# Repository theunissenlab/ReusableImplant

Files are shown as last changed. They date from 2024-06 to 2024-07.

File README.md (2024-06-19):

# Chronic Reusable Implant Parts List and Instructions

Both .stl and .sldprt files have been included for your convinence. All SLDPRT files were made on SOLIDWORKS 2022.

## Implant Parts List

In this repository are all the parts required to build the chronic implant. It is made for use with the Cambridge Neurotech Mini-Amp and silicon probes. All parts were printed on FormLabs Form 3+. Specific printing instructions including resin type, density, and touchpoint size are detailed depending on the part.

- [Payload](https://github.com/AnnLiBenn/ReusableImplant/blob/main/README.md#payload)
- [Docking](https://github.com/AnnLiBenn/ReusableImplant/blob/main/README.md#Docking)
- [Amplifier Holder](https://github.com/AnnLiBenn/ReusableImplant/blob/main/README.md#amplifier-holder)
- [Headstage Cover](https://github.com/AnnLiBenn/ReusableImplant/blob/main/README.md#headstage-cover)
- [Payload Holder](https://github.com/AnnLiBenn/ReusableImplant/blob/main/README.md#payload-holder)
- [Docking Holder](https://github.com/AnnLiBenn/ReusableImplant/blob/main/README.md#docking-holder)
- [Support Base](https://github.com/AnnLiBenn/ReusableImplant/blob/main/README.md#support-base)

### Payload

This is the module that holds the probe. It is re-used across implantations. Print in Rigid resin with density at 80 and touchpoint size at 0.4mm.

<p align="center">
Screenshot 2024-06-19 at 3 01 42 PM

</p>

### Docking

This is the module that is cemented to the skull after being screwed to the payload module. A new docking module is required for each implantation. Print in Rigid resin with density at 80 and touchpoint size at 0.4mm.

<p align="center">
Screenshot 2024-06-19 at 3 02 54 PM

</p>

### Amplifier Holder

This is the module that inserts into the payload in order to hold and stablilize the amplifier. It is re-used across implantations. Print in Rigid resin with density at 80 and touchpoint size at 0.4mm.

<p align="center">
Screenshot 2024-06-19 at 3 03 33 PM

</p>

### Headstage Cover

This is the cover for the implant. It protects the flex cable between the probe and amplifier. It is re-used across implantations. Print in Black resin with density 90 and touchpoint size at 0.4mm.

<p align="center">
Screenshot 2024-06-19 at 3 04 15 PM

</p>

### Assembly Jig Parts List

In this section are all the parts needed to create the jig for assembly.

## Payload Holder

This is a holder that can is inserted into the payload module during assembly so that the payload module is centered. Print in Black resin with density 80 and touchpoint size at 0.45mm.

<p align="center">
Screenshot 2024-06-19 at 3 06 48 PM

</p>

### Docking Holder

This is a holder that holds the docking module in place when using the jig to combine the two modules. Print in Black resin with density 80 and touchpoint size at 0.45mm.

<p align="center">
Screenshot 2024-06-19 at 3 07 34 PM

</p>

### Support Base

This is the base of the assembly jig. It is used to secure the rods. Print in Black resin with density 80 and touchpoint size at 0.45mm.

<p align="center">
Screenshot 2024-06-19 at 3 07 56 PM
</p>

### Rod Attachment

This is an attachment for a rod to hold the payload module. Print in Black resin density 80 and touchpoint size 0.40mm.

<p align="center">
Screenshot 2024-06-19 at 3 11 28 PM
</p>

### Assembly Diagrams

This is the complete implant assembly.

<p align="center">
Screenshot 2024-06-19 at 3 09 19 PM
Screenshot 2024-06-19 at 3 10 05 PM

</p>

## Additional Parts:

Note: Links are for reference, but could be sourced elsewhere. The brass inserts are heat inserted using a soldering iron and mild pressure.

- [M1 Brass knurled inserts](https://www.ebay.co.uk/itm/124738465135) (5x): To be heat-inserted into the Payload.

- [M3 Brass knurled inserts](https://www.mcmaster.com/94459A140/) (6x): To be heat-inserted into the Docking Holder and support base.
  
- [M1 Screws](https://www.mcmaster.com/91800A050/) (5x): To lock modules together.

- [M3 10mm screws](https://www.mcmaster.com/91290A295/) (6x): For securing the Docking Module in its holder, and the rods in the support base

- 6.4mm diameter rods: For creating the assembly jig

## Cleaning Instructions

This is a cleaning cap for the cleaning of the probes after use. It is designed to screw on to 20mL vial.

<p align="center">
Screenshot 2024-06-19 at 3 10 26 PM

</p>

## Note
All .sldprt files were created using SOLIDWORKS 2022. This design is inspired by the [Coen-Lab Apollo Implant](https://github.com/Coen-Lab/chronic-neuropixels/tree/main#np1_payload-or-np2-alpha_payload).

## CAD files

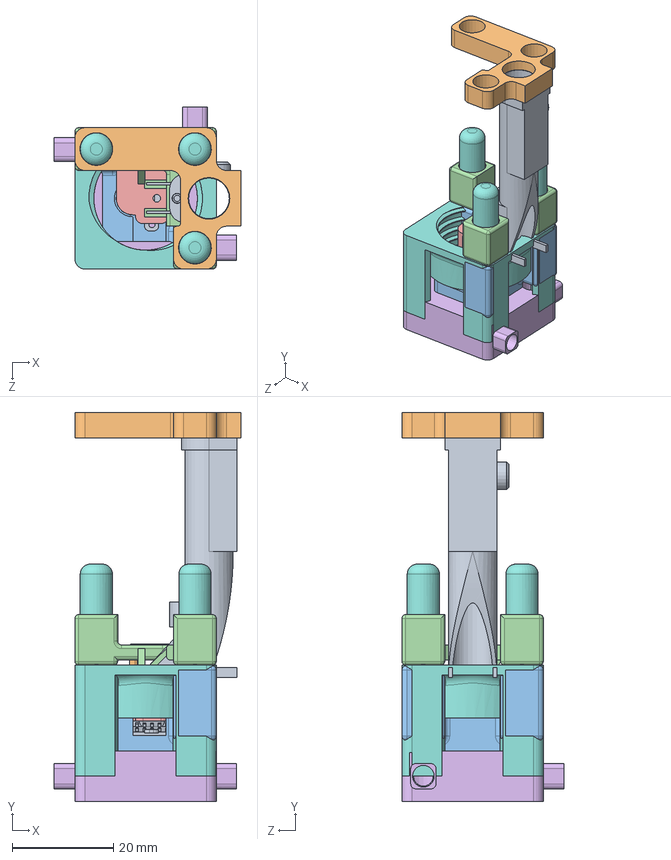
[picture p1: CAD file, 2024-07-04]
ImplantSLDPRT/HeadstageAssembly.SLDASM
36.9 x 77.0 x 32.1 mm
SupportBase
Payload
RodAttachmentRigid
RodGuide

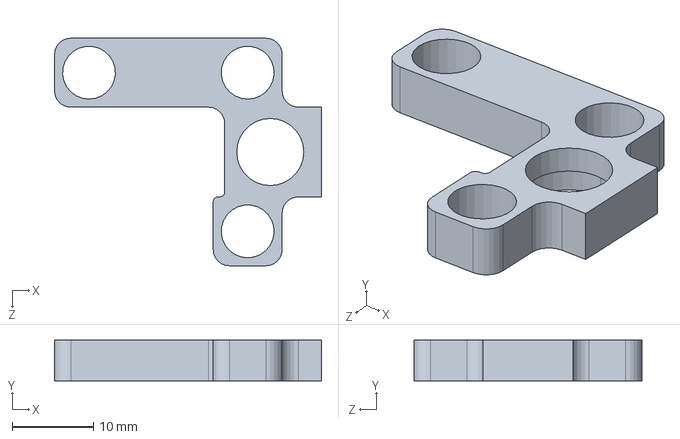
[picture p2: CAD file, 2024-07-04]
ImplantSLDPRT/RodGuide.SLDPRT
32.8 x 5.00 x 28.0 mm

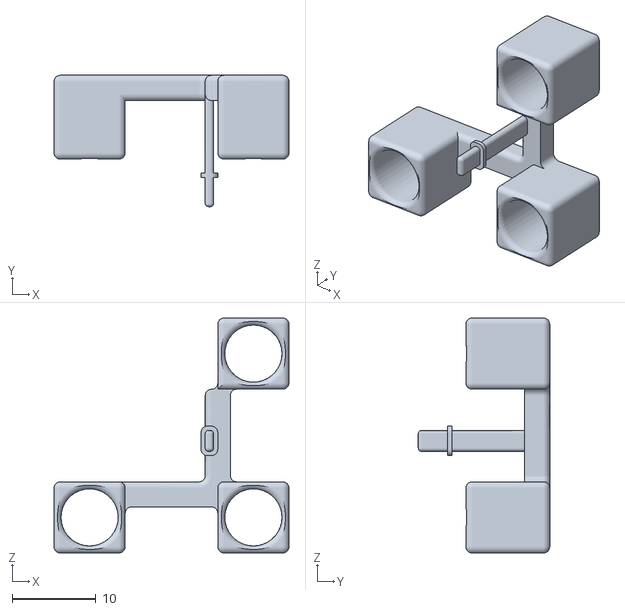
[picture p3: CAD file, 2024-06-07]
ImplantSTL/Payload Holder v3.STL
28.0 x 15.7 x 28.0

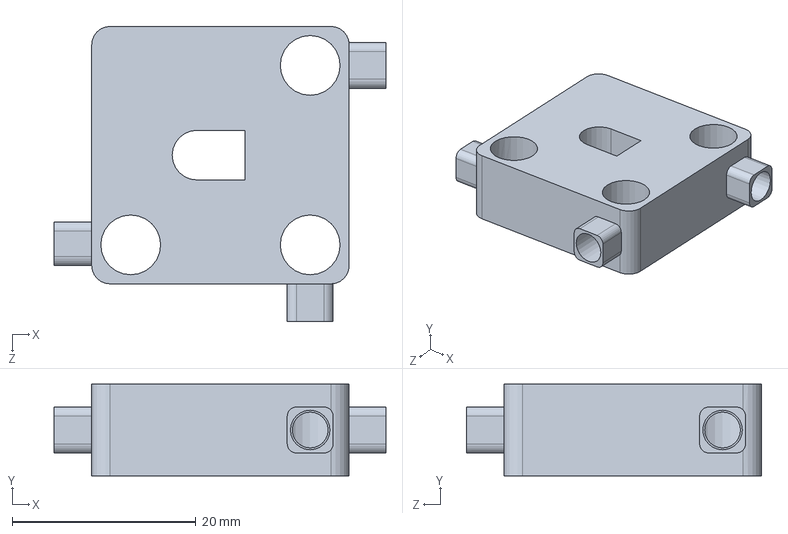
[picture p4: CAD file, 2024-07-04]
ImplantSLDPRT/SupportBase.SLDPRT
36.1 x 10.0 x 32.1 mm

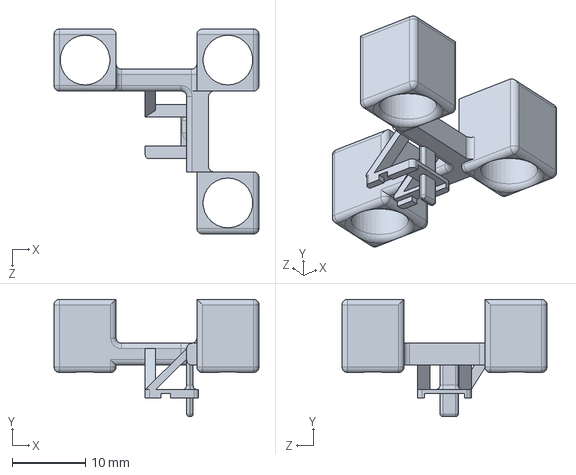
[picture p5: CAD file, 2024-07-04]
ImplantSLDPRT/PayloadHolder.SLDPRT
28.0 x 16.0 x 28.0 mm

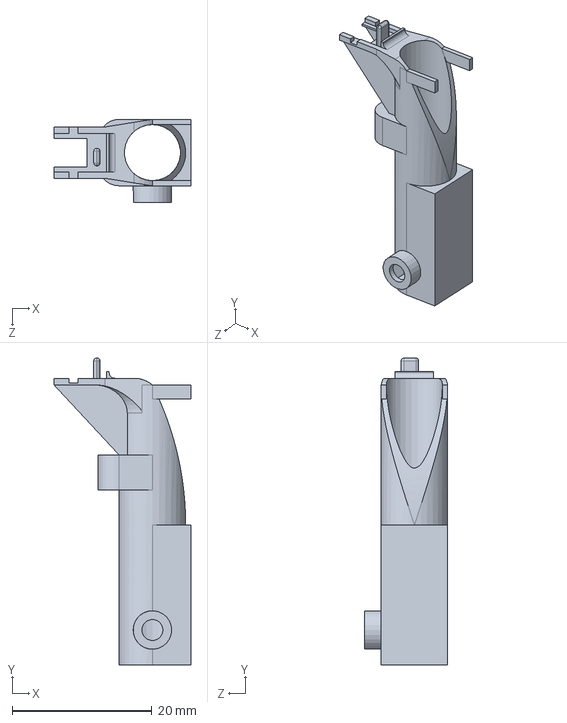
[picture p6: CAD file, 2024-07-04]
ImplantSLDPRT/RodAttachment.SLDPRT
19.6 x 43.9 x 11.9 mm

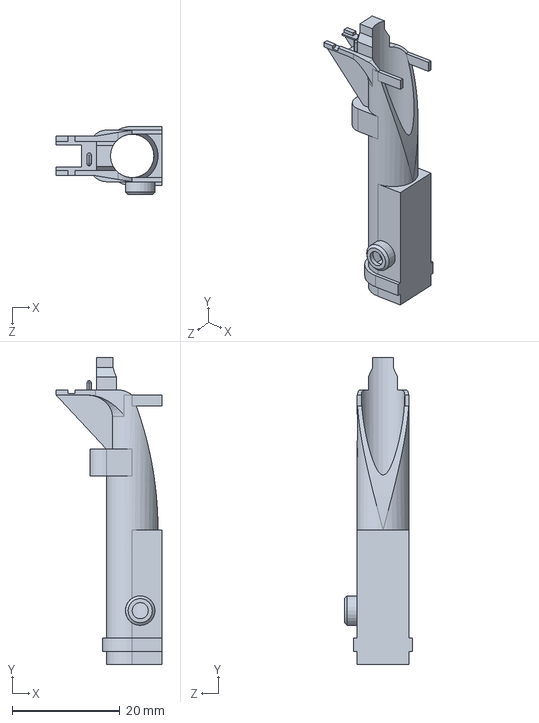
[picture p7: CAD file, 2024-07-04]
ImplantSLDPRT/RodAttachmentRigid.SLDPRT
19.6 x 57.0 x 12.7 mm

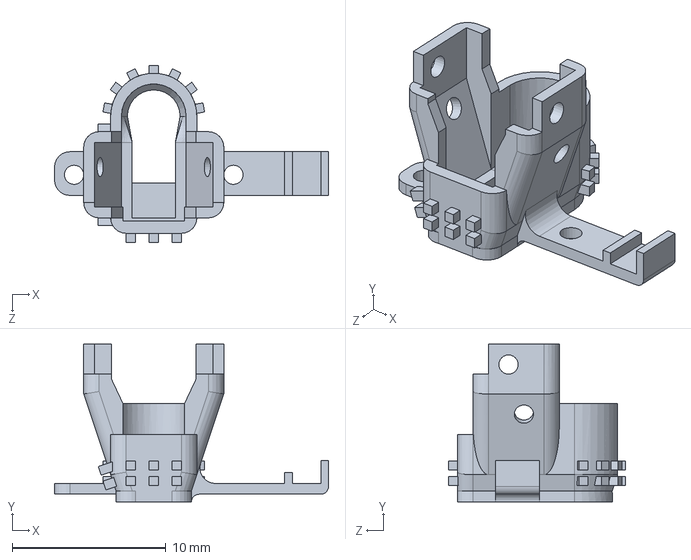
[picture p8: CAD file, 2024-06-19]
ImplantSLDPRT/Docking.SLDPRT
17.8 x 10.2 x 11.5 mm

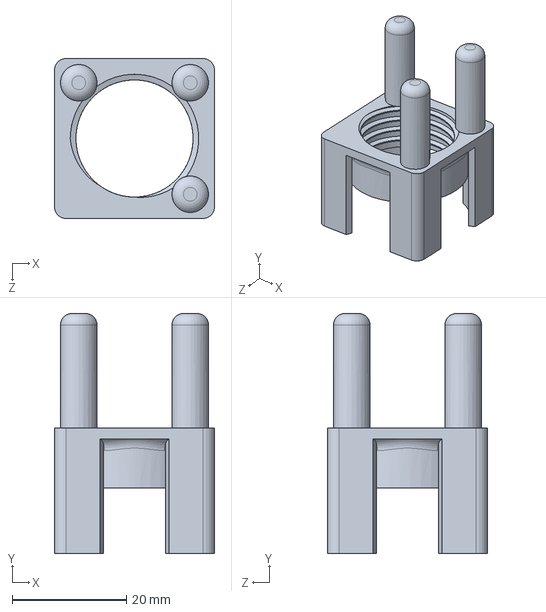
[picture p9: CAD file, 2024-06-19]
ImplantSLDPRT/CleaningCap.SLDPRT
28.0 x 42.0 x 28.0 mm

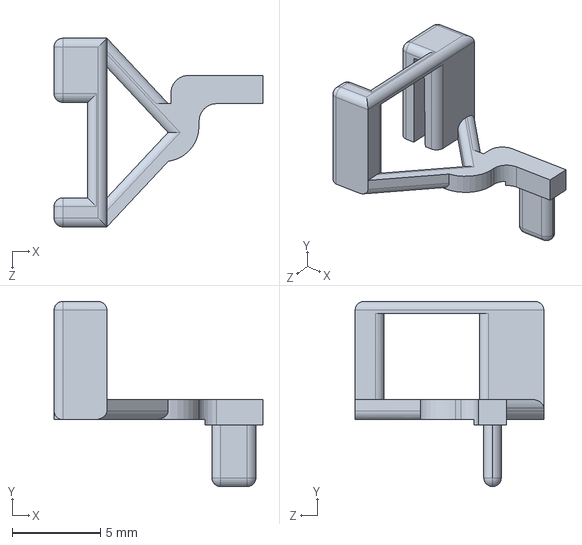
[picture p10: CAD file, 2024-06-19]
ImplantSLDPRT/AmplifierHolder.SLDPRT
11.8 x 10.5 x 10.7 mm

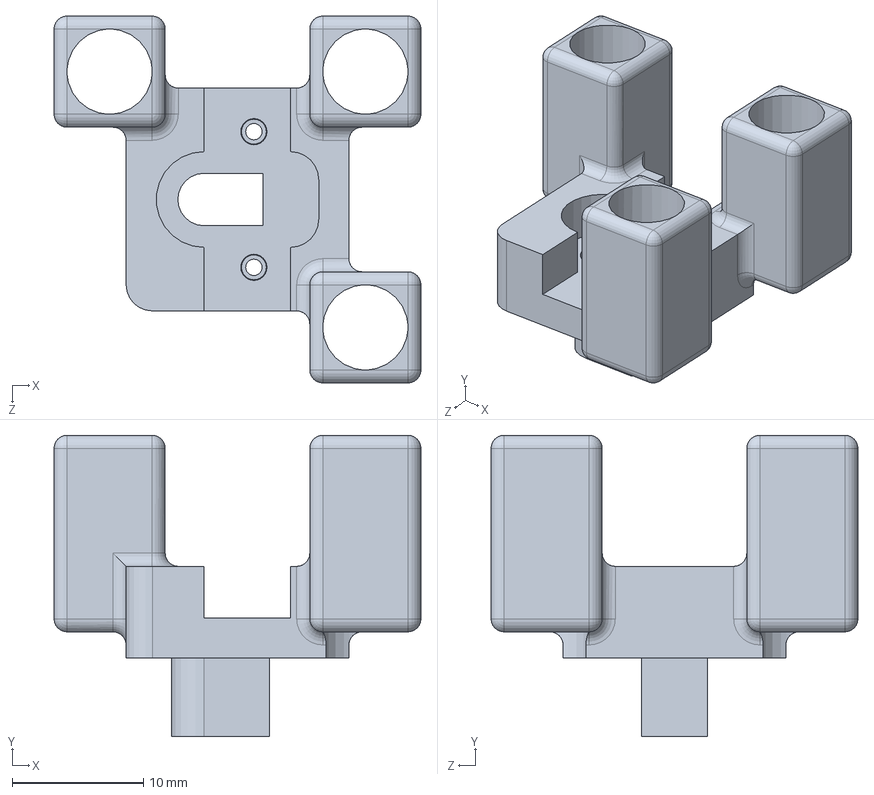
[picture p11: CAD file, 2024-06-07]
ImplantSLDPRT/Docking Holder v3.SLDPRT
28.0 x 23.0 x 28.0 mm

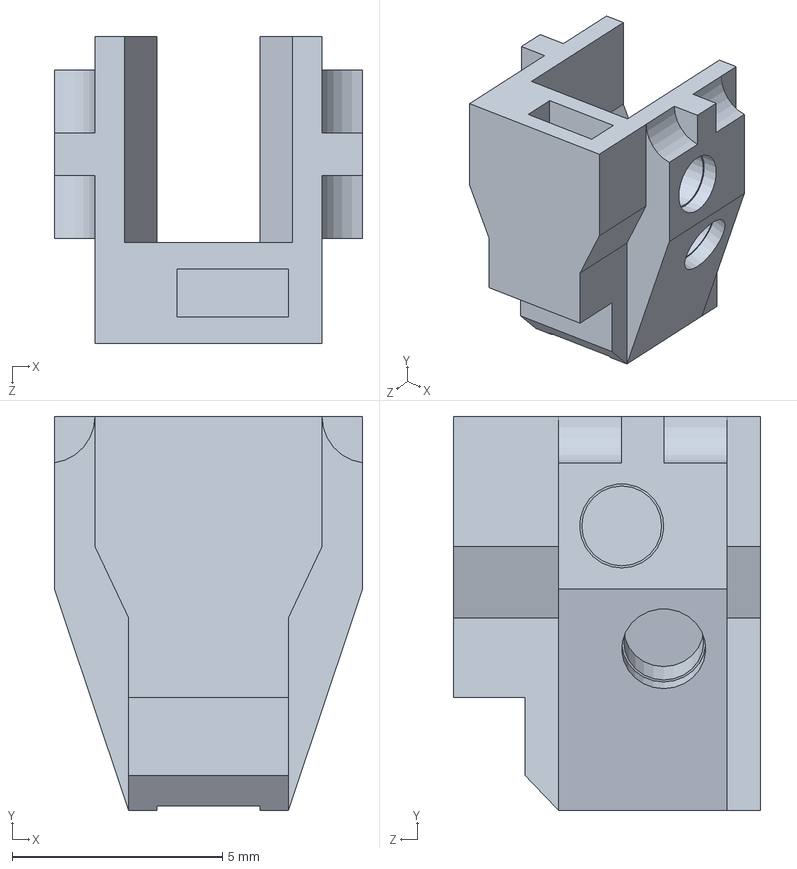
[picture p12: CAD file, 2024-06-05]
ImplantSLDPRT/Payload.SLDPRT
7.33 x 9.37 x 7.30 mm

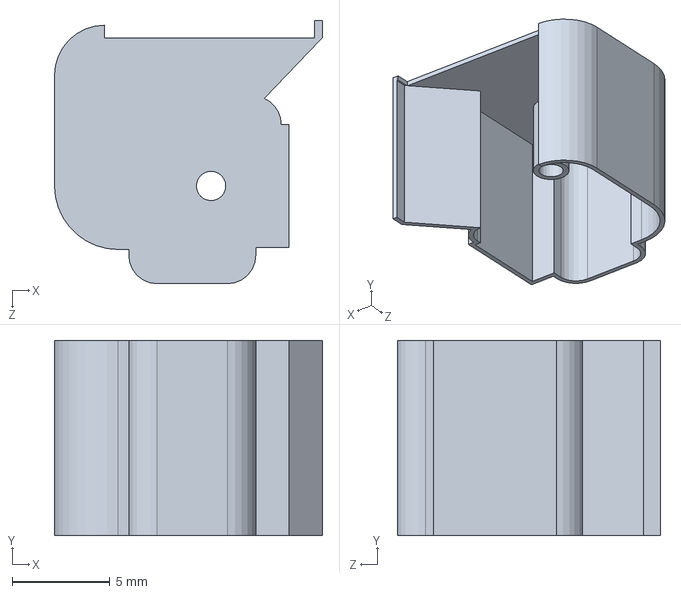
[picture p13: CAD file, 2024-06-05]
ImplantSLDPRT/HeadstageCover.SLDPRT
13.7 x 10.0 x 13.5 mm

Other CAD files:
ImplantSLDPRT/Docking v4 (with support).SLDPRT
ImplantSLDPRT/Support Base.SLDPRT
ImplantSTL/AmplifierHolder.STL
ImplantSTL/CleaningCap.STL
ImplantSTL/Docking Holder v3.STL
ImplantSTL/Docking v4 (with support).STL
ImplantSTL/Docking.STL
ImplantSTL/DockingHolder.STL
ImplantSTL/HeadstageCover.STL
ImplantSTL/Payload.STL
ImplantSTL/PayloadHolder.STL
ImplantSTL/RodAttachment.STL
ImplantSTL/RodAttachmentRigid.STL
ImplantSTL/RodGuide.STL
ImplantSTL/Support Base.STL
ImplantSTL/SupportBase.STL

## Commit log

2024-06-05 Add files via upload
    SLDPRT files
    [AmplifierHolder.SLDPRT, Docking.SLDPRT, DockingHolder.SLDPRT, HeadstageCover.SLDPRT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]
2024-06-05 Rename Support Base.SLDPRT to SupportBase.SLDPRT
    [SupportBase.SLDPRT]
2024-06-05 Rename Support Base.STL to SupportBase.STL
    [SupportBase.STL]
2024-06-07 Rename Docking Holder v3.STL to DockingHolder.STL
    [DockingHolder.STL]
2024-06-07 Rename Docking v4 (with support).STL to Docking.STL
    [Docking.STL]
2024-06-07 Rename Payload Holder v3.STL to PayloadHolder.STL
    [PayloadHolder.STL]
2024-06-07 Rename Docking Holder v3.SLDPRT to DockingHolder.SLDPRT
    [DockingHolder.SLDPRT]
2024-06-07 Rename Docking v4 (with support).SLDPRT to Docking.SLDPRT
    [Docking.SLDPRT]
2024-06-07 Rename Payload Holder v3.SLDPRT to Payload Holder.SLDPRT
    [Payload Holder.SLDPRT]
